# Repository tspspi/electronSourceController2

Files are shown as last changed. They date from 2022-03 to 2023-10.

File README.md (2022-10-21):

# Electron gun power supply and monitoring controller

_Note_: This project is designed for a particular experiment so it will not
be much of use for anyone who's not working on exactly that experiment.

This is firmware for a simple electron gun controller that is controlling

* Up to four FUG HCP 14-6500 high voltage power supplies (acceleration
  voltage, Wehnelt cylinder, focus voltage and a single deflection voltage
  power supply)
* The voltage and current measured by FUG HCP 14-6500 can also be used for
  general monitoring and beam loss measurement

## External communication ports

* UART0 provides main communication interface (and is also used by avrdude
  during flashing - there is an Arduino bootloader flashed on the board so
  flash method ```ẁiring``` can be used via USB

* Other UARTs may be used for RS485 or other components later on

## Pin assignment

| Pin | Assignment                          | Mode                      | ATEMGA2560 Port / Pin |
| --- | ----------------------------------- | ------------------------- | --------------------- |
| 22  | PSU1: Output enable                 | Digital out (optocoupled) | PA0                   |
| 23  | PSU1: Polarity set                  | Digital out (optocoupled) | PA1                   |
| 24  | PSU1: Current control mode          | Digital in                | PA2                   |
| 25  | PSU1: Voltage control mode          | Digital in                | PA3                   |
| 42  | PSU1: Voltage set                   | Analog out                | PL7                   |
| 43  | PSU1: Current limit set             | Analog out                | PL6                   |
| A0  | PSU1: Voltage sense                 | Analog in                 | PF0                   |
| A1  | PSU1: Current sense                 | Analog in                 | PF1                   |
| 26  | PSU2: Output enable                 | Digital out (optocoupled) | PA4                   |
| 27  | PSU2: Polarity set                  | Digital out (optocoupled) | PA5                   |
| 28  | PSU2: Current control mode          | Digital in                | PA6                   |
| 29  | PSU2: Voltage control mode          | Digital in                | PA7                   |
| 44  | PSU2: Voltage set                   | Analog out                | PL5                   |
| 45  | PSU2: Current limit set             | Analog out                | PL4                   |
| A2  | PSU2: Voltage sense                 | Analog in                 | PF2                   |
| A3  | PSU2: Current sense                 | Analog in                 | PF3                   |
| 30  | PSU3: Output enable                 | Digital out (optocoupled) | PC7                   |
| 31  | PSU3: Polarity set                  | Digital out (optocoupled) | PC6                   |
| 32  | PSU3: Current control mode          | Digital in                | PC5                   |
| 33  | PSU3: Voltage control mode          | Digital in                | PC4                   |
| 46  | PSU3: Voltage set                   | Analog out                | PL3                   |
| 47  | PSU3: Current limit set             | Analog out                | PL2                   |
| A4  | PSU3: Voltage sense                 | Analog in                 | PF4                   |
| A5  | PSU3: Current sense                 | Analog in                 | PF5                   |
| 34  | PSU4: Output enable                 | Digital out (optocoupled) | PC3                   |
| 35  | PSU4: Polarity set                  | Digital out (optocoupled) | PC2                   |
| 36  | PSU4: Current control mode          | Digital in                | PC1                   |
| 37  | PSU4: Voltage control mode          | Digital in                | PC0                   |
| 48  | PSU4: Voltage set                   | Analog out                | PL1                   |
| 49  | PSU4: Current limit set             | Analog out                | PL0                   |
| A6  | PSU4: Voltage sense                 | Analog in                 | PF6                   |
| A7  | PSU4: Current sense                 | Analog in                 | PF7                   |
| 38  | Filament power supply (230V side)   | Digital out               | PD7                   |
| A8  | Current sensor for filament         | Analog in                 | PK0                   |
| 50  | AD7705 MISO                         | Digital in                | PB3                   |
| 51  | AD7705 MOSI                         | Digital out               | PB2                   |
| 52  | AD7705 SCK                          | Digital out               | PB1                   |
| 53  | AD7705 CS                           | Digital out               | PB0                   |
|PWM10| AD7705 Reset                        | Digital out               | PB4                   |
|PWM11| AD7705 data ready                   | Digital in                | PB5                   |

## Protocol

In contrast to other implementations this board supports an ASCII based
communication protocol. For synchronization all messages start with a
fixed synchronization pattern consisting of three dollar signs. Each command
is terminated via a CR LF or only LF (CR is simply ignored by the serial
parser). Numbers are transmitted as ASCII decimal numbers.

| Command                                 | Sequence               | Response                                                                                                                     | Status                           |
| --------------------------------------- | ---------------------- | ---------------------------------------------------------------------------------------------------------------------------- | -------------------------------- |
| ID                                      | $$$ID<LF>              | Sends a simple ID response that identifies the firmware (ex. ```$$$electronctrl_20210707_001<LF>```)                         | working, tested                  |
| Filament on                             | $$$FILON<LF>           | Switches filament power supply on                                                                                            | working, tested                  |
| Filament off                            | $$$FILOFF<LF>          | Switches filament power supply off                                                                                           | working, tested                  |
| Estimate beam current                   | $$$BEAMA<LF>           | Calculates estimated beam current in 1/10 of microamperes                                                                    |                                  |
| Beam on                                 | $$$BEAMON<LF>          | Switches beam high voltage on (slowly, performing insulation test)                                                           | working, tested                  |
| Beam HV off                             | $$$BEAMHVOFF<LF>       | Switches beam high voltage off                                                                                               | working, tested                  |
| Get PSU current                         | $$$PSUGETA[n]<LF>      | Gets current for power supply 1,2,3,4                                                                                        | working, tested                  |
| Get PSU voltage                         | $$$PSUGETV[n]<LF>      | Gets voltage for power supply 1,2,3,4                                                                                        | working, tested                  |
| Get PSU modes                           | $$$PSUMODE<LF>         | Gets the mode for each PSU as a sequence of 4 ASCII chars (A or V for current or voltage controled mode, - for disabled)     | working, tested                  |
| Set PSU current limit                   | $$$PSUSETA[n][mmm]<LF> | Sets the power supply current limit for one of the 4 PSUs. The limit is supplied in 1/10 of an microampere                   | working, tested                  |
| Set PSU target voltage                  | $$$PSUSETV[n][mmm]<LF> | Sets the power supply voltage for one of the 4 PSUs. The voltage is set in V                                                 | working, tested                  |
| Set PSU polarity                        | $$$PSUPOL[n][p/n]<LF>  | Sets the polarity to be positive or negative                                                                                 | working, tested                  |
| Set PSU output enable                   | $$$PSUON[n]<LF>        | Enabled the output of the given PSU                                                                                          | working, tested                  |
| Set PSU output disable                  | $$$PSUOFF[n]<LF>       | Disabled the output of the given PSU                                                                                         | working, tested                  |
| Disable all voltages (PSU and filament) | $$$OFF<LF>             | Disabled all voltages including the filament supply                                                                          | working, tested                  |
| Get filament voltage                    | $$$FILV<LF>            | Measures filament voltage (if supported)                                                                                     |                                  |
| Get filament current                    | $$$FILA<LF>            | Measures filament current (if supported)                                                                                     |                                  |
| Set filament current                    | $$$SETFILA[n]<LF>      | Sets filament current via current controller board                                                                           |                                  |
| Perform HV insulation test              | $$$INSUL<LF>           | Performs insulation test. Reports voltages while testing.                                                                    | working, tested                  |
| Perform cathode bakeout                 | $$$FILBAKE<LF>         | Performs a baking sequence on filament to remove any residue of trapped gas on the surface                                   |                                  |
| Perform software reset                  | $$$RESET<LF>           | Performs a software reset on the control system (reinitializes everything, no power cycle)                                   |                                  |

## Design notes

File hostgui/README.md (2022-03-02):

# Custom electron gun slow control Python communication library and GUI utlity

__Work in progress__

## Communication library

The communication library from ```eguncom.py``` implements most of the
communication protocol with the electron beam slow-control system.

### ```class ElectronGunControl```

The ```ElectronGunControl``` class implements asynchronous and synchronous
communication with the serially / USB attached control system. The port file
is passed to the constructor

```
ctrl = ElectronGunNotConnected(portFile = '/dev/...')
```

When no port file is passed it defaults to ```/dev/ttyU0```.

The exposed public methods are:

| Method                            | Description                                                                                                        | Synchronous      | Asynchronous callback                                |
| --------------------------------- | ------------------------------------------------------------------------------------------------------------------ | ---------------- | ---------------------------------------------------- |
| id()                              | Queries the current version                                                                                        | with sync = True | cbIdentify(controller, versionDate, versionRevision) |
| getPSUVoltage(channel)            | Queries the current voltage on the given channel                                                                   | with sync = True | cbVoltage(controller, channel, voltageVolts)         |
| getPSUCurrent(channel)            | Queries the current current on the given channel                                                                   | with sync = True | cbCurrent(controller, channel, currentMicroamps)     |
| getPSUModes()                     | Checks if PSUs are off, in voltage limited or current limited mode                                                 | with sync = True | cbPSUMode(controller, states)                        |
| getFilamentCurrent()              | Queries the filament current                                                                                       | with sync = True | cbFilamentCurrent(controller, current)               |
| off()                             | Disabled all high voltage and filament currents                                                                    |                  |                                                      |
| setPSUPolarity(channel, polarity) | Sets polarity to POLARITY_POS or POLARITY_NEG                                                                      |                  |                                                      |
| setPSUEnable(channel)             | Enables the given PSU channel                                                                                      |                  |                                                      |
| setPSUDisable(channel)            | Disables the given PSU channel                                                                                     |                  |                                                      |
| setPSUVoltage(channel, voltage)   | Sets the given channel to the given voltage                                                                        |                  |                                                      |
| setFilamentCurrent(currentMa)     | Sets the filament current or target current to the specified milliamps                                             |                  |                                                      |
| setFilamentOn()                   | Enabled the filament supply                                                                                        |                  |                                                      |
| setFilamentOff()                  | Disabled the filament supply                                                                                       |                  |                                                      |
| runInsulationTest()               | Runs an insulation test with low current limits                                                                    | with sync = True | cbInsulation(isOk, listOfShorts)                     |
| beamOn()                          | Runs the slow beam on sequence (slowly heating filament to previously set setFilamentCurrent, ramping up voltages) | with sync = True | cbBeamon()                                           |

### Usage example

#### Synchronous sample (USB / serial)

Example to perform a __synchronous__:

* Insulation check
* Startup for 100 mA beam current
* Looping through focus voltages
* Shutting down

```
with ElectronGunControl() as ctrl:
    # Currently a hack to wait for the control system to reset when using the
    # primary port

    time.sleep(5)

    # We want to see the voltages reported by the system so we
    # define a lambda that just prints the voltages while ramping up
    # during insulation test and beam on sequence

    ctrl.cbVoltage = lambda c,chan,v : print("Voltage for channel {} is {} V".format(chan, v))

    # Query it's identity
    ret = ctrl.id(sync = True)
    print("ID call returned {}".format(ret))

    # Run insulation test
    print("Running insulation test")
    ret = ctrl.runInsulationTest(sync = True)
    print("Insulation test returned: {}".format(ret))

    # Run beam on sequence ...
    ret = ctrl.beamOn(sync = True)
    print("Beam on successfully returned: {}".format(ret))

    print("Sweeping focus voltage")
    for focusVoltage in range(1750,1950):
        print("New focus voltage {}".format(focusVoltage))
        ctrl.setPSUVoltage(3, focusVoltage)
        time.sleep(1)

    ctrl.off()
    print("Off, done ...")
```

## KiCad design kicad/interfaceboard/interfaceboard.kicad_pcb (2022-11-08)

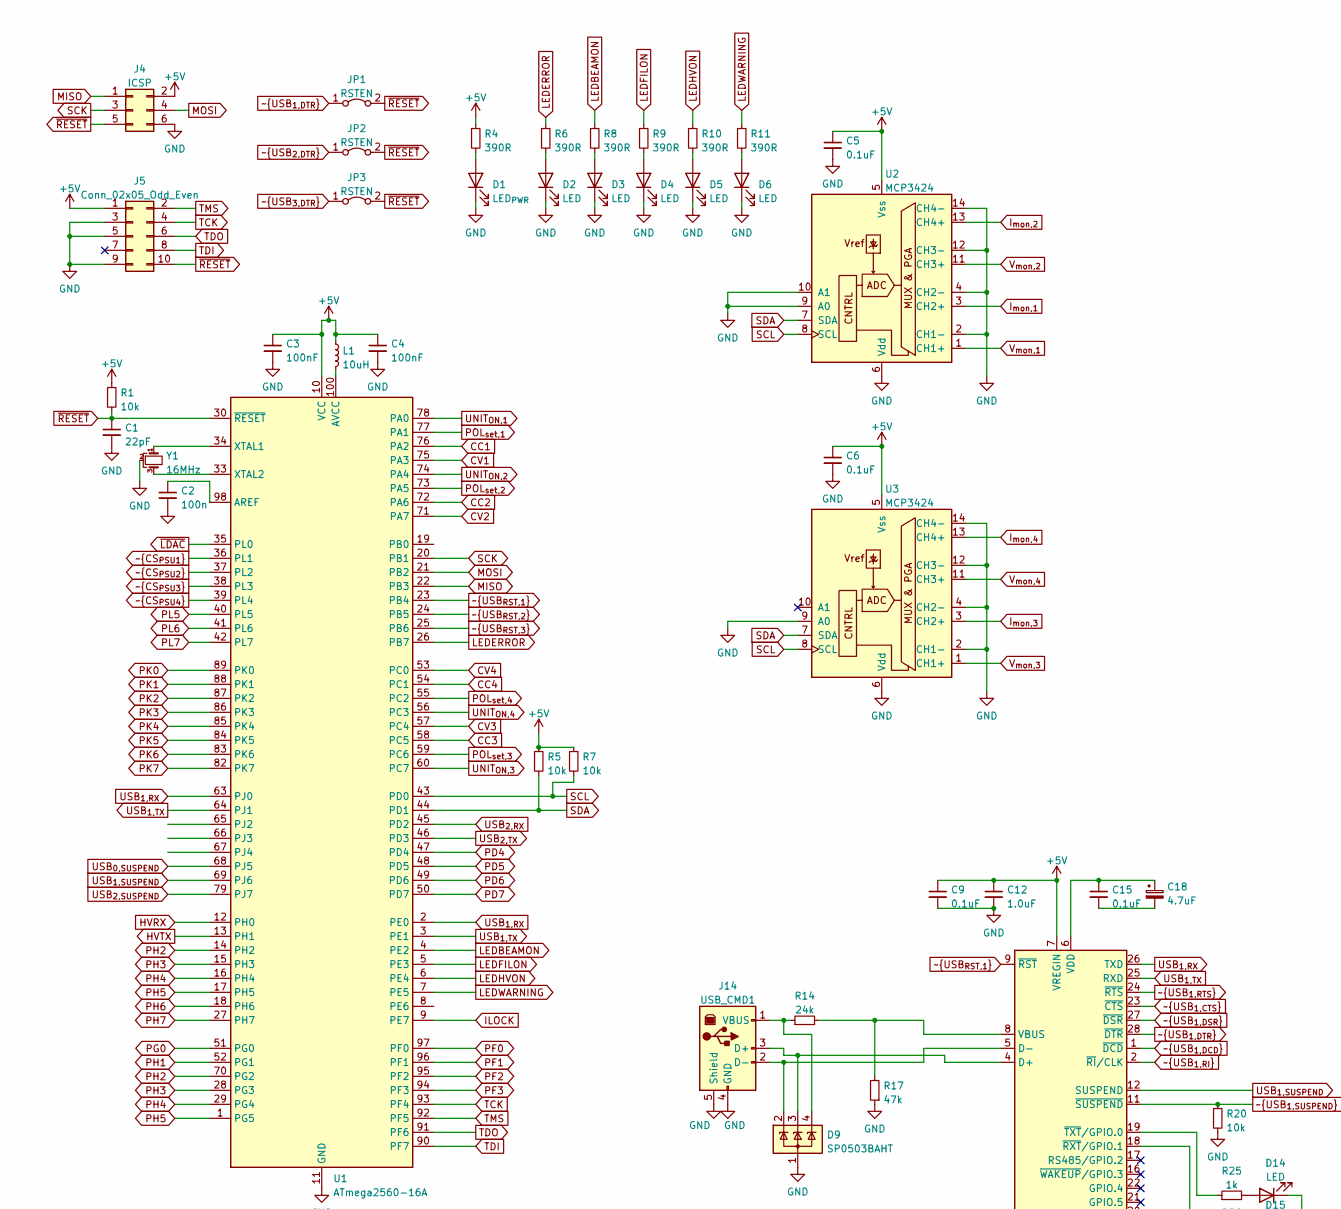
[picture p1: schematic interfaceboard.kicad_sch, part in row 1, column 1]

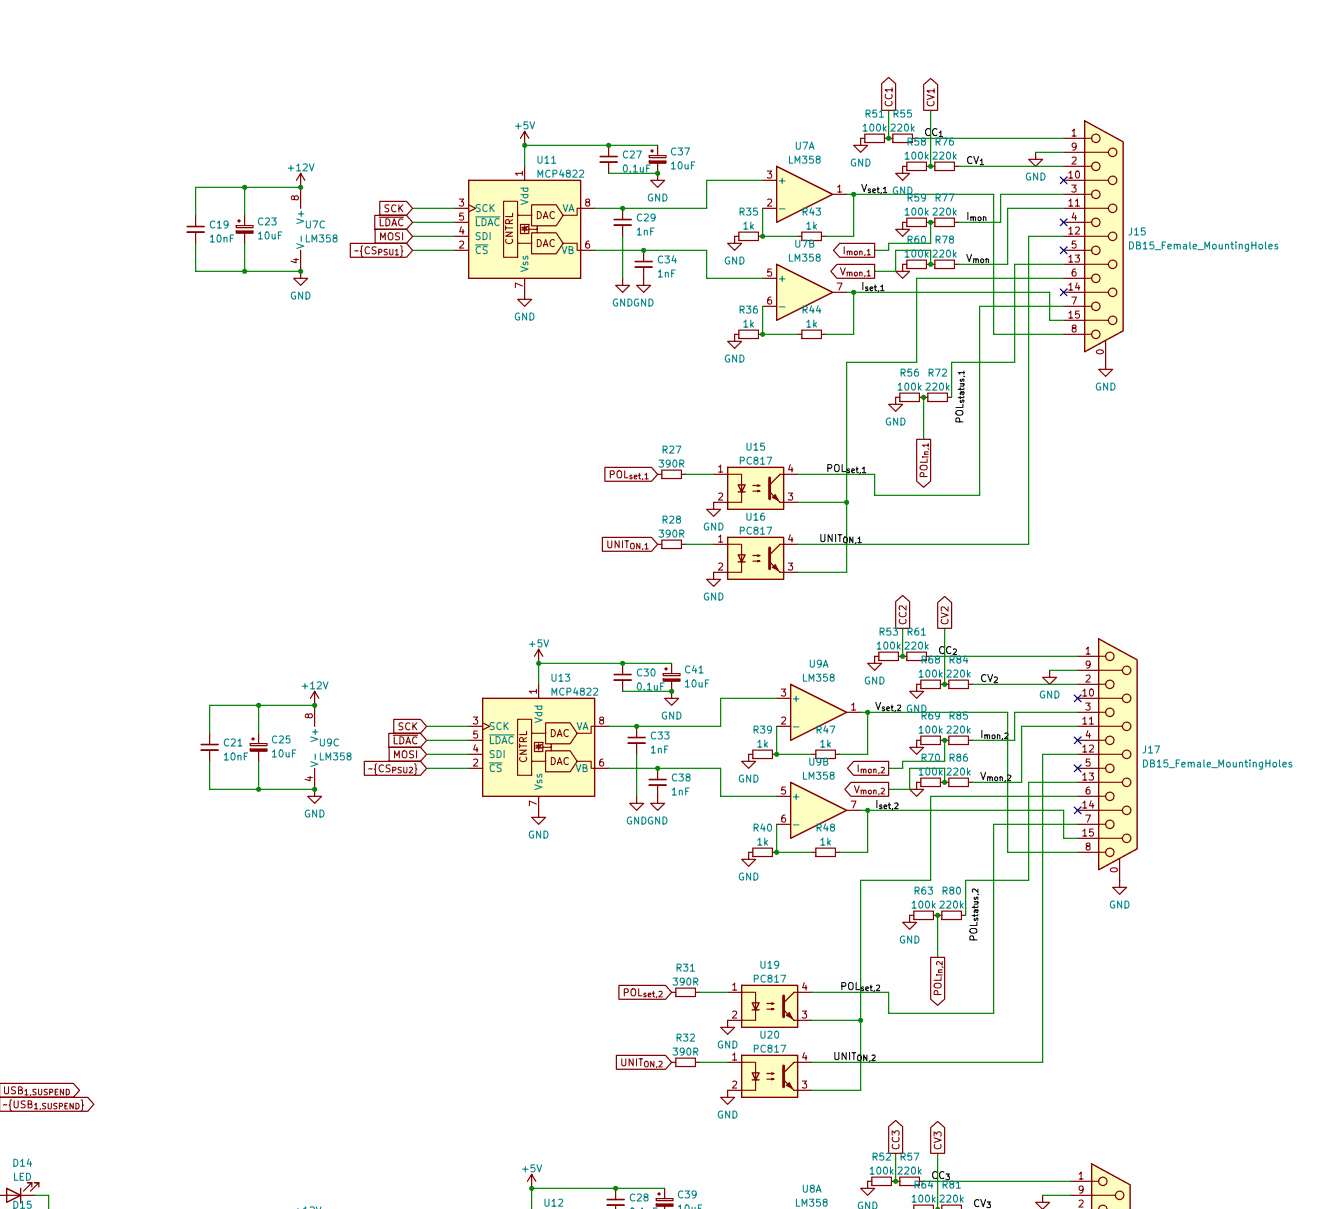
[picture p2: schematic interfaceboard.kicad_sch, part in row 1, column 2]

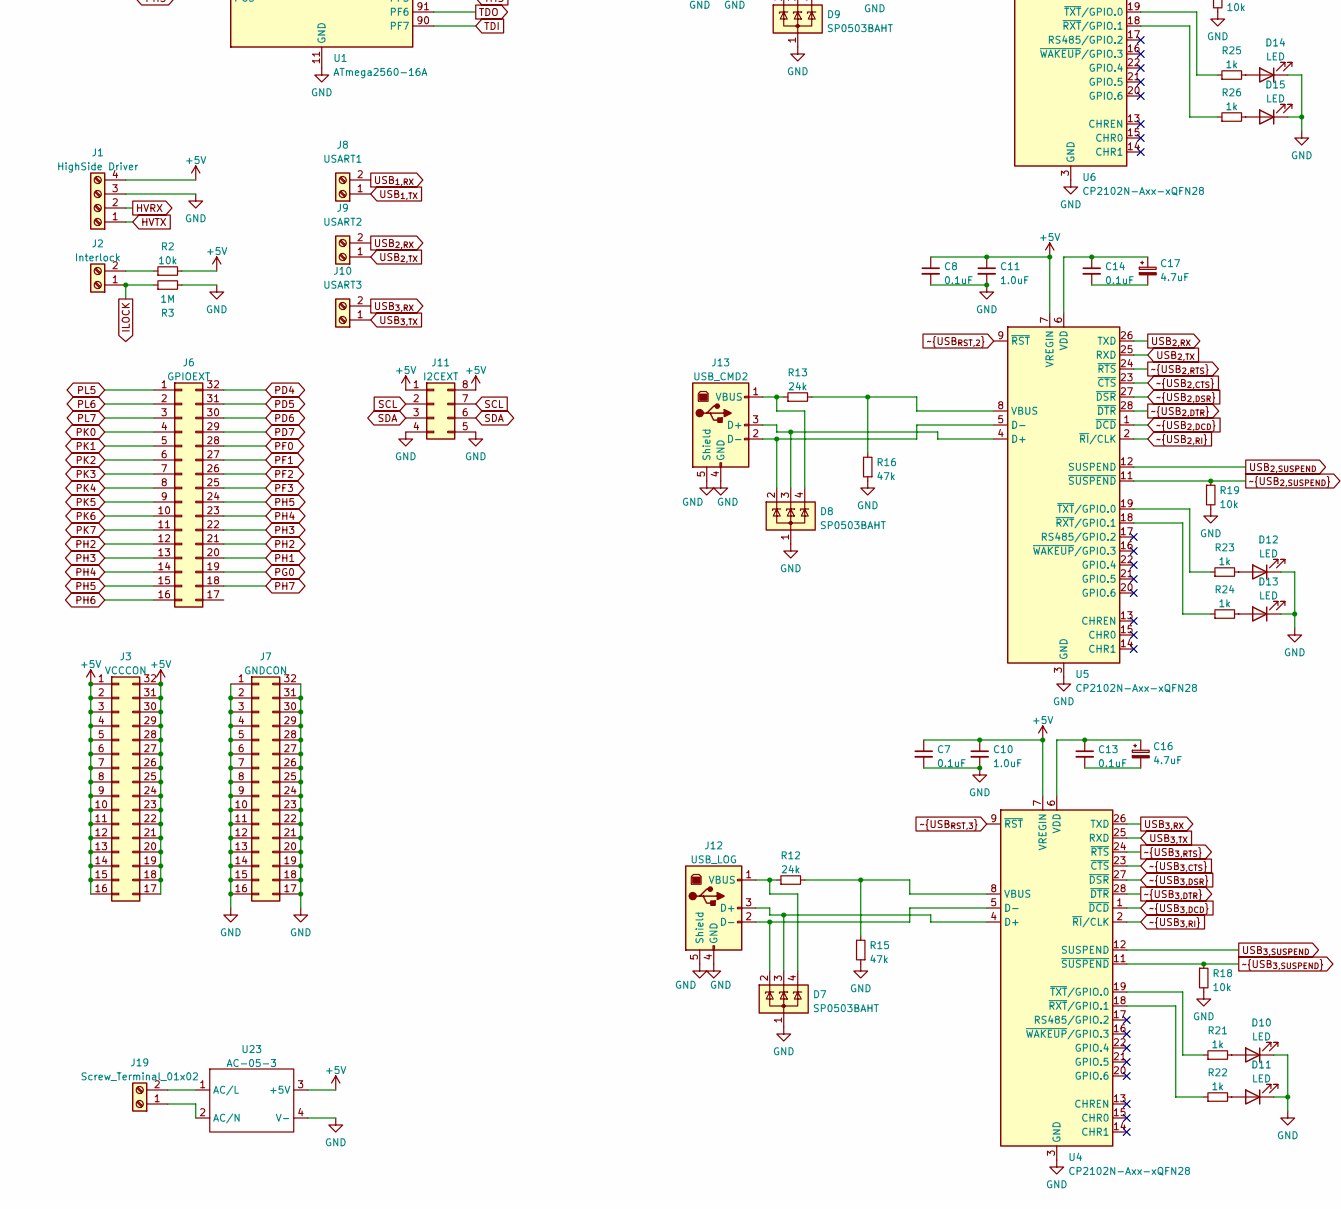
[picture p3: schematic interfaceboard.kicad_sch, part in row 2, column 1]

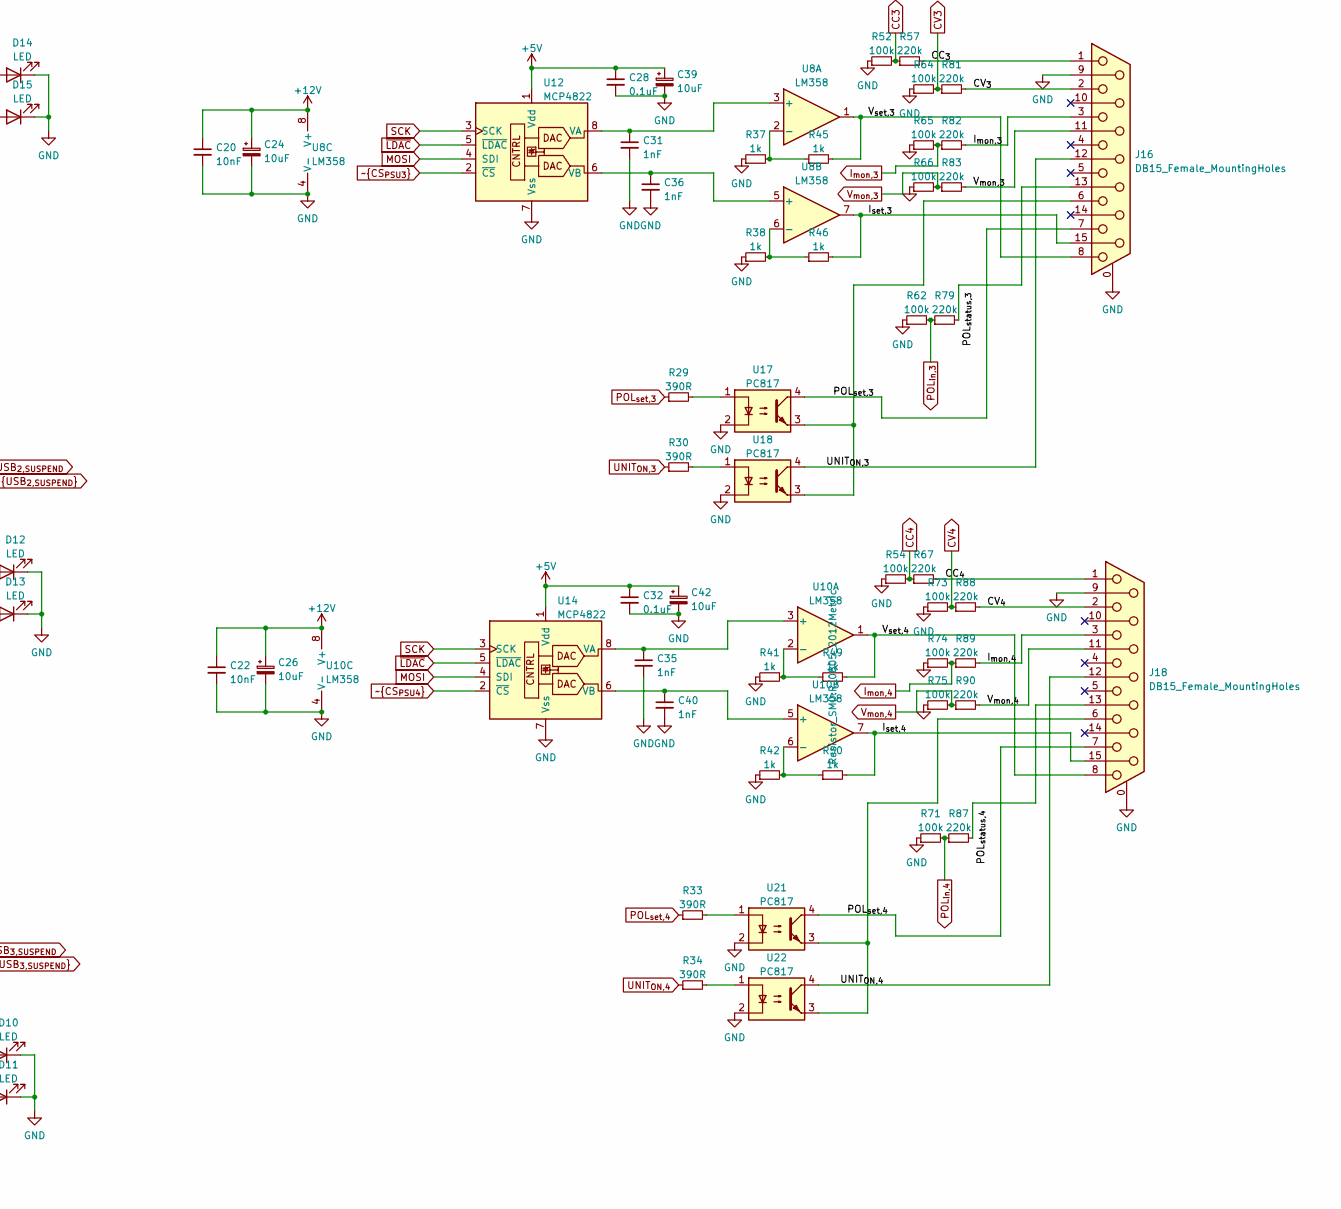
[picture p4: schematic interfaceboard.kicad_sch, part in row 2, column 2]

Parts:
C1: 22pF; C_0805_2012Metric
C2: 100n; C_0805_2012Metric
C3, C4: 100nF; C_0805_2012Metric
C5, C6, C7, C8, C9, C13, C14, C15, C27, C28, C30, C32: 0.1uF; C_0805_2012Metric
C10, C11, C12: 1.0uF; C_0805_2012Metric
C16, C17, C18: 4.7uF; C_0805_2012Metric
C19, C20, C21, C22: 10nF; C_0805_2012Metric
C23, C24, C25, C26, C37, C39, C41, C42: 10uF; C_0805_2012Metric
C29, C31, C33, C34, C35, C36, C38, C40: 1nF; C_0805_2012Metric
D1: LED_{PWR}; LED_D3.0mm
D2, D3, D4, D5, D6, D10, D11, D12, D13, D14, D15: LED; LED_D3.0mm
D7, D8, D9: SP0503BAHT; SOT-143
J1: HighSide Driver; PinHeader_1x04_P2.54mm_Vertical
J2: Interlock; PinHeader_1x02_P2.54mm_Vertical
J3: VCCCON; PinHeader_2x16_P2.54mm_Vertical
J4: ICSP; PinSocket_2x03_P2.54mm_Vertical
J5: Conn_02x05_Odd_Even; PinSocket_2x05_P2.54mm_Vertical
J6: GPIOEXT; PinHeader_2x16_P2.54mm_Vertical
J7: GNDCON; PinHeader_2x16_P2.54mm_Vertical
J8: USART1; PinHeader_1x02_P2.54mm_Vertical
J9: USART2; PinHeader_1x02_P2.54mm_Vertical
J10: USART3; PinHeader_1x02_P2.54mm_Vertical
J11: I2CEXT; PinHeader_2x04_P2.54mm_Vertical
J12: USB_LOG; USB_B_Lumberg_2411_02_Horizontal; FarnellNo 3490505 (2401 06)
J13: USB_CMD2; USB_B_Lumberg_2411_02_Horizontal
J14: USB_CMD1; USB_B_Lumberg_2411_02_Horizontal
J15: DB15_Female_MountingHoles; DSUB-15_Female_Horizontal_P2.77x2.84mm_EdgePinOffset9.90mm_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; FarnellNo 3817870
J16, J17, J18: DB15_Female_MountingHoles; DSUB-15_Female_Horizontal_P2.77x2.84mm_EdgePinOffset9.90mm_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
J19: Screw_Terminal_01x02; PinHeader_1x02_P2.54mm_Vertical
JP1, JP2, JP3: RSTEN; PinSocket_1x02_P2.54mm_Vertical
L1: 10uH; L_1206_3216Metric
R1, R2, R5, R7, R18, R19, R20: 10k; R_0805_2012Metric
R3: 1M; R_0805_2012Metric
R4, R6, R8, R9, R10, R11, R27, R28, R29, R30, R31, R32, R33, R34: 390R; R_0805_2012Metric
R12, R13, R14: 24k; R_0805_2012Metric
R15, R16, R17: 47k; R_0805_2012Metric
R21, R22, R23, R24, R25, R26, R35, R36, R37, R38, R39, R40, R41, R42, R43, R44, R45, R46, R47, R48, R49, R50: 1k; R_0805_2012Metric
R51, R52, R53, R54, R56, R58, R59, R60, R62, R63, R64, R65, R66, R68, R69, R70, R71, R73, R74, R75: 100k; R_0805_2012Metric
R55, R57, R61, R67, R72, R76, R77, R78, R79, R80, R81, R82, R83, R84, R85, R86, R87, R88, R89, R90: 220k; R_0805_2012Metric
U1: ATmega2560-16A; TQFP-100_14x14mm_P0.5mm
U2, U3: MCP3424; SOIC-14_3.9x8.7mm_P1.27mm
U4, U5, U6: CP2102N-Axx-xQFN28; QFN-28-1EP_5x5mm_P0.5mm_EP3.35x3.35mm
U7, U8, U9, U10: LM358; DIP-8_W7.62mm
U11, U12, U13, U14: MCP4822; DIP-8_W7.62mm
U15, U16, U17, U18, U19, U20, U21, U22: PC817; DIP-4_W7.62mm
U23: AC-05-3
Y1: 16MHz; PinSocket_1x03_P2.54mm_Vertical

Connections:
+5V: C3.1, C4.1, C5.1, C6.1, C7.1, C8.1, C9.1, C10.1, C11.1, C12.1, C27.1, C28.1, C30.1, C32.1, C37.1, C39.1, C41.1, C42.1, J1.4, J3.1, J3.2, J3.3, J3.4, J3.5, J3.6, J3.7, J3.8, J3.9, J3.10, J3.11, J3.12, J3.13, J3.14, J3.15, J3.16, J3.17, J3.18, J3.19, J3.20, J3.21, J3.22, J3.23, J3.24, J3.25, J3.26, J3.27, J3.28, J3.29, J3.30, J3.31, J3.32, J4.2, J5.1, J11.1, J11.8, L1.1, R1.1, R2.2, R4.1, R5.1, R7.1, U1.10 (VCC), U1.31 (VCC), U1.61 (VCC), U1.80 (VCC), U2.5 (Vss), U3.5 (Vss), U4.7 (VREGIN), U5.7 (VREGIN), U6.7 (VREGIN), U11.1 (Vdd), U12.1 (Vdd), U13.1 (Vdd), U14.1 (Vdd), U23.3 (+5V)
+12V: C19.1, C20.1, C21.1, C22.1, C23.1, C24.1, C25.1, C26.1, U7.8 (V+), U8.8 (V+), U9.8 (V+), U10.8 (V+)
/CC_{1}: J15.1, R55.2
/CC_{2}: J17.1, R61.2
/CC_{3}: J16.1, R57.2
/CC_{4}: J18.1, R67.2
/CV_{1}: J15.2, R76.2
/CV_{2}: J17.2, R84.2
/CV_{3}: J16.2, R81.2
/CV_{4}: J18.2, R88.2
/I_{mon}: J15.3, R77.2
/I_{set,1}: J15.15, R44.2, U7.7
/I_{set,2}: J17.15, R48.2, U9.7
/I_{set,3}: J16.15, R46.2, U8.7
/I_{set,4}: J18.15, R50.2, U10.7
/V_{mon}: J15.11 (P111), R78.2
/V_{set,1}: J15.8, R43.2, U7.1
/V_{set,2}: J17.8, R47.2, U9.1
/V_{set,3}: J16.8, R45.2, U8.1
/V_{set,4}: J18.8, R49.2, U10.1
CC1: R51.2, R55.1, U1.76 (PA2)
CC2: R53.2, R61.1, U1.72 (PA6)
CC3: R52.2, R57.1, U1.58 (PC5)
CC4: R54.2, R67.1, U1.54 (PC1)
CV1: R58.2, R76.1, U1.75 (PA3)
CV2: R68.2, R84.1, U1.71 (PA7)
CV3: R64.2, R81.1, U1.57 (PC4)
CV4: R73.2, R88.1, U1.53 (PC0)
GND: C1.2, C2.2, C3.2, C4.2, C5.2, C6.2, C7.2, C8.2, C9.2, C10.2, C11.2, C12.2, C19.2, C20.2, C21.2, C22.2, C23.2, C24.2, C25.2, C26.2, C27.2, C28.2, C29.2, C30.2, C31.2, C32.2, C33.2, C34.2, C35.2, C36.2, C37.2, C38.2, C39.2, C40.2, C41.2, C42.2, D1.1 (K), D2.1 (K), D3.1 (K), D4.1 (K), D5.1 (K), D6.1 (K), D7.1 (A), D8.1 (A), D9.1 (A), D10.1 (K), D11.1 (K), D12.1 (K), D13.1 (K), D14.1 (K), D15.1 (K), J1.3, J4.6, J5.3, J5.5, J5.9, J7.1, J7.2, J7.3, J7.4, J7.5, J7.6, J7.7, J7.8, J7.9, J7.10, J7.11, J7.12, J7.13, J7.14, J7.15, J7.16, J7.17, J7.18, J7.19, J7.20, J7.21, J7.22, J7.23, J7.24, J7.25, J7.26, J7.27, J7.28, J7.29, J7.30, J7.31, J7.32, J11.4, J11.5, J12.4 (GND), J12.5 (Shield), J13.4 (GND), J13.5 (Shield), J14.4 (GND), J14.5 (Shield), J15.0 (PAD), J15.9, J16.0 (PAD), J16.9, J17.0 (PAD), J17.9, J18.0 (PAD), J18.9, R3.2, R15.1, R16.1, R17.1, R18.2, R19.2, R20.2, R35.1, R36.1, R37.1, R38.1, R39.1, R40.1, R41.1, R42.1, R51.1, R52.1, R53.1, R54.1, R56.1, R58.1, R59.1, R60.1, R62.1, R63.1, R64.1, R65.1, R66.1, R68.1, R69.1, R70.1, R71.1, R73.1, R74.1, R75.1, U1.11 (GND), U1.32 (GND), U1.62 (GND), U1.81 (GND), U1.99 (GND), U2.2 (CH1-), U2.4 (CH2-), U2.6 (Vdd), U2.9 (A0), U2.10 (A1), U2.12 (CH3-), U2.14 (CH4-), U3.2 (CH1-), U3.4 (CH2-), U3.6 (Vdd), U3.9 (A0), U3.12 (CH3-), U3.14 (CH4-), U4.3 (GND), U4.29 (GND), U5.3 (GND), U5.29 (GND), U6.3 (GND), U6.29 (GND), U7.4 (V-), U8.4 (V-), U9.4 (V-), U10.4 (V-), U11.7 (Vss), U12.7 (Vss), U13.7 (Vss), U14.7 (Vss), U15.2, U16.2, U17.2, U18.2, U19.2, U20.2, U21.2, U22.2, U23.4 (V-), Y1.2
HVRX: J1.2, U1.12 (PH0)
HVTX: J1.1, U1.13 (PH1)
ILOCK: J2.1, R3.1, U1.9 (PE7)
I_{mon,1}: R59.2, R77.1, U2.3 (CH2+)
I_{mon,2}: J17.3, R69.2, R85.1, R85.2, U2.13 (CH4+)
I_{mon,3}: J16.3, R65.2, R82.1, R82.2, U3.3 (CH2+)
I_{mon,4}: J18.3, R74.2, R89.1, R89.2, U3.13 (CH4+)
LEDBEAMON: R8.1, U1.4 (PE2)
LEDERROR: R6.1, U1.26 (PB7)
LEDFILON: R9.1, U1.5 (PE3)
LEDHVON: R10.1, U1.6 (PE4)
LEDWARNING: R11.1, U1.7 (PE5)
MISO: J4.1, U1.22 (PB3)
MOSI: J4.4, U1.21 (PB2), U11.4 (SDI), U12.4 (SDI), U13.4 (SDI), U14.4 (SDI)
unnamed: C2.1, U1.98 (AREF)
unnamed: C13.1, C16.1, U4.6 (VDD)
unnamed: C13.2, C16.2
unnamed: C14.1, C17.1, U5.6 (VDD)
unnamed: C14.2, C17.2
unnamed: C15.1, C18.1, U6.6 (VDD)
unnamed: C15.2, C18.2
unnamed: C29.1, U7.3 (+), U11.8 (VA)
unnamed: C31.1, U8.3 (+), U12.8 (VA)
unnamed: C33.1, U9.3 (+), U13.8 (VA)
unnamed: C34.1, U7.5 (+), U11.6 (VB)
unnamed: C35.1, U10.3 (+), U14.8 (VA)
unnamed: C36.1, U8.5 (+), U12.6 (VB)
unnamed: C38.1, U9.5 (+), U13.6 (VB)
unnamed: C40.1, U10.5 (+), U14.6 (VB)
unnamed: D1.2 (A), R4.2
unnamed: D2.2 (A), R6.2
unnamed: D3.2 (A), R8.2
unnamed: D4.2 (A), R9.2
unnamed: D5.2 (A), R10.2
unnamed: D6.2 (A), R11.2
unnamed: D7.2 (K), J12.2 (D-), U4.5 (D-)
unnamed: D7.3 (K), J12.3 (D+), U4.4 (D+)
unnamed: D7.4 (K), J12.1 (VBUS), R12.1
unnamed: D8.2 (K), J13.2 (D-), U5.5 (D-)
unnamed: D8.3 (K), J13.3 (D+), U5.4 (D+)
unnamed: D8.4 (K), J13.1 (VBUS), R13.1
unnamed: D9.2 (K), J14.2 (D-), U6.5 (D-)
unnamed: D9.3 (K), J14.3 (D+), U6.4 (D+)
unnamed: D9.4 (K), J14.1 (VBUS), R14.1
unnamed: D10.2 (A), R21.2
unnamed: D11.2 (A), R22.2
unnamed: D12.2 (A), R23.2
unnamed: D13.2 (A), R24.2
unnamed: D14.2 (A), R25.2
unnamed: D15.2 (A), R26.2
unnamed: J2.2, R2.1
unnamed: J15.6, U15.3, U16.3
unnamed: J15.13, R72.2
unnamed: J16.6, U17.3, U18.3
unnamed: J16.13, R79.2
unnamed: J17.6, U19.3, U20.3
unnamed: J17.13, R80.2
unnamed: J18.6, U21.3, U22.3
unnamed: J18.13, R87.2
unnamed: J19.1, U23.2 (AC/N)
unnamed: J19.2, U23.1 (AC/L)
unnamed: L1.2, U1.100 (AVCC)
unnamed: R12.2, R15.2, U4.8 (VBUS)
unnamed: R13.2, R16.2, U5.8 (VBUS)
unnamed: R14.2, R17.2, U6.8 (VBUS)
unnamed: R21.1, U4.19 (~TXT/GPIO.0)
unnamed: R22.1, U4.18 (~RXT/GPIO.1)
unnamed: R23.1, U5.19 (~TXT/GPIO.0)
unnamed: R24.1, U5.18 (~RXT/GPIO.1)
unnamed: R25.1, U6.19 (~TXT/GPIO.0)
unnamed: R26.1, U6.18 (~RXT/GPIO.1)
unnamed: R27.2, U15.1
unnamed: R28.2, U16.1
unnamed: R29.2, U17.1
unnamed: R30.2, U18.1
unnamed: R31.2, U19.1
unnamed: R32.2, U20.1
unnamed: R33.2, U21.1
unnamed: R34.2, U22.1
unnamed: R35.2, R43.1, U7.2 (-)
unnamed: R36.2, R44.1, U7.6 (-)
unnamed: R37.2, R45.1, U8.2 (-)
unnamed: R38.2, R46.1, U8.6 (-)
unnamed: R39.2, R47.1, U9.2 (-)
unnamed: R40.2, R48.1, U9.6 (-)
unnamed: R41.2, R49.1, U10.2 (-)
unnamed: R42.2, R50.1, U10.6 (-)
unnamed: U1.33 (XTAL2), Y1.3
unnamed: U1.34 (XTAL1), Y1.1
PD4: J6.32, U1.47 (PD4)
PD5: J6.31, U1.48 (PD5)
PD6: J6.30, U1.49 (PD6)
PD7: J6.29, U1.50 (PD7)
PF0: J6.28, U1.97 (PF0)
PF1: J6.27, U1.96 (PF1)
PF2: J6.26, U1.95 (PF2)
PF3: J6.25, U1.94 (PF3)
PG0: J6.19, U1.51 (PG0)
PH1: J6.20, U1.52 (PG1)
PH2: J6.12, J6.21, U1.14 (PH2), U1.70 (PG2)
PH3: J6.13, J6.22, U1.15 (PH3), U1.28 (PG3)
PH4: J6.14, J6.23, U1.16 (PH4), U1.29 (PG4)
PH5: J6.15, J6.24, U1.1 (PG5), U1.17 (PH5)
PH6: J6.16, U1.18 (PH6)
PH7: J6.18, U1.27 (PH7)
PK0: J6.4, U1.89 (PK0)
PK1: J6.5, U1.88 (PK1)
PK2: J6.6, U1.87 (PK2)
PK3: J6.7, U1.86 (PK3)
PK4: J6.8, U1.85 (PK4)
PK5: J6.9, U1.84 (PK5)
PK6: J6.10, U1.83 (PK6)
PK7: J6.11, U1.82 (PK7)
PL5: J6.1, U1.40 (PL5)
PL6: J6.2, U1.41 (PL6)
PL7: J6.3, U1.42 (PL7)
POL_{in,1}: R56.2, R72.1
POL_{in,2}: R63.2, R80.1
POL_{in,3}: R62.2, R79.1
POL_{in,4}: R71.2, R87.1
POL_{set,1}: J15.7, R27.1, U1.77 (PA1), U15.4
POL_{set,2}: J17.7, R31.1, U1.73 (PA5), U19.4
POL_{set,3}: J16.7, R29.1, U1.59 (PC6), U17.4
POL_{set,4}: J18.7, R33.1, U1.55 (PC2), U21.4
SCK: J4.3, U1.20 (PB1), U11.3 (SCK), U12.3 (SCK), U13.3 (SCK), U14.3 (SCK)
SCL: J11.2, J11.7, R7.2, U1.43 (PD0), U2.8 (SCL), U3.8 (SCL)
SDA: J11.3, J11.6, R5.2, U1.44 (PD1), U2.7 (SDA), U3.7 (SDA)
TCK: J5.4, U1.93 (PF4)
TDI: J5.8, U1.90 (PF7)
TDO: J5.6, U1.91 (PF6)
TMS: J5.2, U1.92 (PF5)
UNIT_{ON,1}: J15.12, R28.1, U1.78 (PA0), U16.4
UNIT_{ON,2}: J17.12, R32.1, U1.74 (PA4), U20.4
UNIT_{ON,3}: J16.12, R30.1, U1.60 (PC7), U18.4
UNIT_{ON,4}: J18.12, R34.1, U1.56 (PC3), U22.4
USB_{0,SUSPEND}: U1.68 (PJ5)
USB_{1,RX}: J8.2, U1.2 (PE0), U1.63 (PJ0), U6.26 (TXD)
USB_{1,SUSPEND}: U1.69 (PJ6), U6.12 (SUSPEND)
USB_{1,TX}: J8.1, U1.3 (PE1), U1.64 (PJ1), U6.25 (RXD)
USB_{2,RX}: J9.2, U1.45 (PD2), U5.26 (TXD)
USB_{2,SUSPEND}: U1.79 (PJ7), U5.12 (SUSPEND)
USB_{2,TX}: J9.1, U1.46 (PD3), U5.25 (RXD)
USB_{3,RX}: J10.2, U4.26 (TXD)
USB_{3,SUSPEND}: U4.12 (SUSPEND)
USB_{3,TX}: J10.1, U4.25 (RXD)
V_{mon,1}: R60.2, R78.1, U2.1 (CH1+)
V_{mon,2}: J17.11 (P111), R70.2, R86.1, R86.2, U2.11 (CH3+)
V_{mon,3}: J16.11 (P111), R66.2, R83.1, R83.2, U3.1 (CH1+)
V_{mon,4}: J18.11 (P111), R75.2, R90.1, R90.2, U3.11 (CH3+)
~CS_{PSU1}: U1.36 (PL1), U11.2 (~CS)
~CS_{PSU2}: U1.37 (PL2), U13.2 (~CS)
~CS_{PSU3}: U1.38 (PL3), U12.2 (~CS)
~CS_{PSU4}: U1.39 (PL4), U14.2 (~CS)
~LDAC: U1.35 (PL0), U11.5 (~LDAC), U12.5 (~LDAC), U13.5 (~LDAC), U14.5 (~LDAC)
~RESET: C1.1, J4.5, J5.10, JP1.2 (B), JP2.2 (B), JP3.2 (B), R1.2, U1.30 (~RESET)
~USB_{1,CTS}: U6.23 (~CTS)
~USB_{1,DCD}: U6.1 (~DCD)
~USB_{1,DSR}: U6.27 (~DSR)
~USB_{1,DTR}: JP1.1 (A), U6.28 (~DTR)
~USB_{1,RI}: U6.2 (~RI/CLK)
~USB_{1,RTS}: U6.24 (~RTS)
~USB_{1,SUSPEND}: R20.1, U6.11 (~SUSPEND)
~USB_{2,CTS}: U5.23 (~CTS)
~USB_{2,DCD}: U5.1 (~DCD)
~USB_{2,DSR}: U5.27 (~DSR)
~USB_{2,DTR}: JP2.1 (A), U5.28 (~DTR)
~USB_{2,RI}: U5.2 (~RI/CLK)
~USB_{2,RTS}: U5.24 (~RTS)
~USB_{2,SUSPEND}: R19.1, U5.11 (~SUSPEND)
~USB_{3,CTS}: U4.23 (~CTS)
~USB_{3,DCD}: U4.1 (~DCD)
~USB_{3,DSR}: U4.27 (~DSR)
~USB_{3,DTR}: JP3.1 (A), U4.28 (~DTR)
~USB_{3,RI}: U4.2 (~RI/CLK)
~USB_{3,RTS}: U4.24 (~RTS)
~USB_{3,SUSPEND}: R18.1, U4.11 (~SUSPEND)
~USB_{RST,1}: U1.23 (PB4), U6.9 (~RST)
~USB_{RST,2}: U1.24 (PB5), U5.9 (~RST)
~USB_{RST,3}: U1.25 (PB6), U4.9 (~RST)

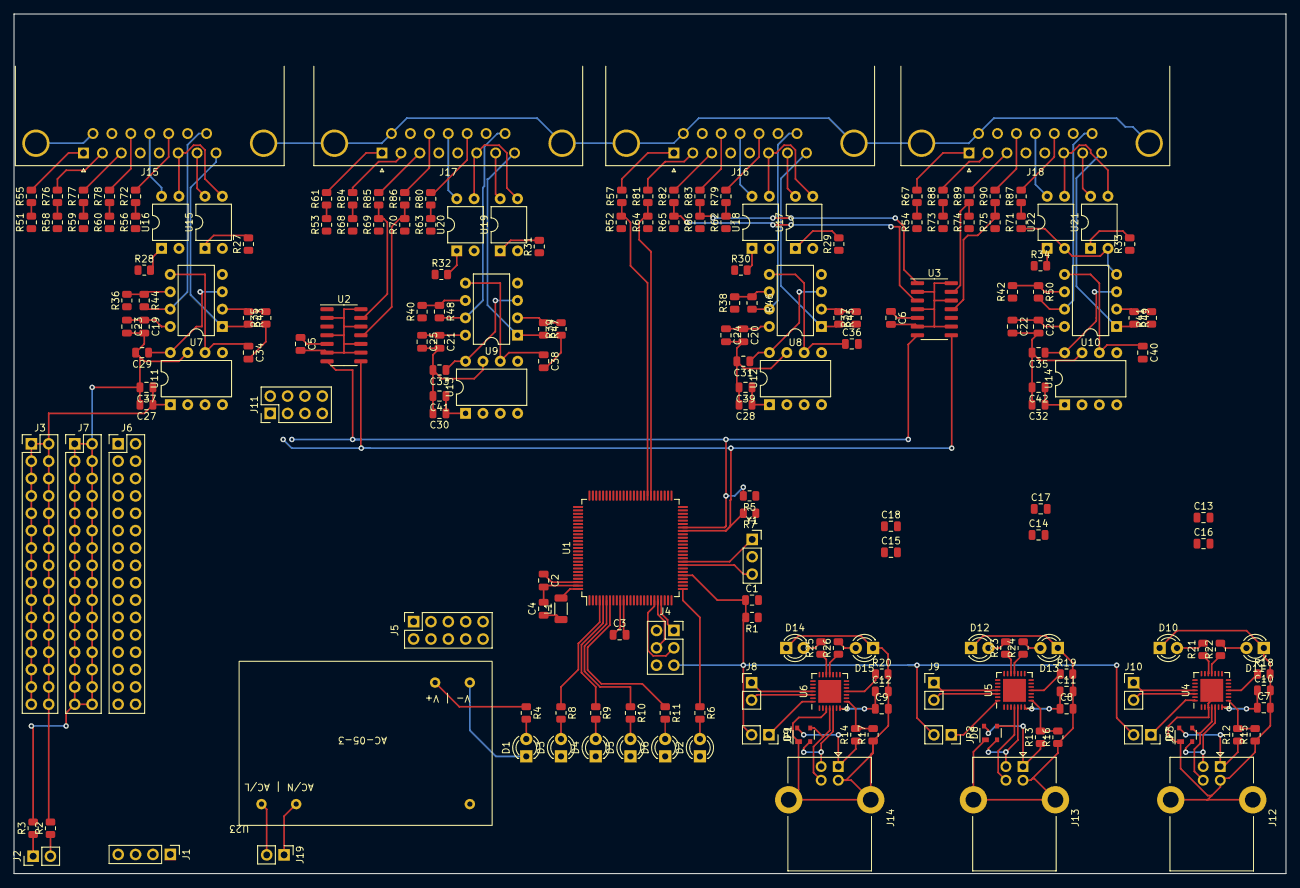
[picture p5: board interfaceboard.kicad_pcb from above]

Board: 2 copper layers, 186.1 x 125.7 mm, 194 parts (0 on the bottom side), 191 nets.

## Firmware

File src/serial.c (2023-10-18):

#include <avr/io.h>
#include <avr/interrupt.h>
#include <math.h>
#include <util/twi.h>
#include <stdint.h>
#include <string.h>

#include "./serial.h"
#include "./controller.h"
#include "./sysclock.h"
#include "./adc.h"
#include "./psu.h"
#include "./pwmout.h"
#include "./cfgeeprom.h"

static void adcCalibrateHVPS_Volts();
static void adcCalibrateHVPS_Amps();

static volatile unsigned long int dwFilament__SetCurrent;
static volatile bool bFilament__EnableCurrent;

/*
    ADC counts to current or voltage:

        HCP 14-6500:        max. 6.5 kV, 2 mA <-> 0...10V

        0...5V <--> 3.25 kV, 1 mA
        5V <-> 1024 ADC counts
        1 ADC count <-> 0.0048828125V
            0.0048828125 <-> 0.003173828125 kV = 3.1738 V
                         <-> 0.0009765625 mA = 0.9765625 uA
*/
/*@
    requires (adcCounts >= 0) && (adcCounts < 1024);
*/
static inline uint16_t serialADC2VoltsHCP(
    uint16_t adcCounts,
    uint8_t channel
) {
    return (uint16_t)(((double)(adcCounts)) * cfgOptions.psuADCCalibration.channel[(channel-1)*2].k + cfgOptions.psuADCCalibration.channel[(channel-1)*2].d);
}
/*@
    requires (adcCounts >= 0) && (adcCounts < 1024);
    assigns \nothing;
*/
static inline uint16_t serialADC2TenthMicroampsHCP(
    uint16_t adcCounts,
    uint8_t channel
) {
    return (uint16_t)(((double)(adcCounts)) * cfgOptions.psuADCCalibration.channel[(channel-1)*2 + 1].k + cfgOptions.psuADCCalibration.channel[(channel-1)*2 + 1].d);
    /* return (uint16_t)((double)(adcCounts) * 9.765625); */
}
static inline uint16_t serialADC2MilliampsFILA(
    uint16_t adcCounts
) {
    uint16_t deviation;
    if(adcCounts < 512) {
        deviation = 512 - adcCounts;
    } else {
        deviation = adcCounts - 512;
    }
    return (uint16_t)(((double)deviation) * 4.8828125);
}

/*
    Ringbuffer utilis
*/
/*@
    predicate acsl_serialbuffer_valid(struct ringBuffer* lpBuf) =
        \valid(lpBuf)
        && \valid(&(lpBuf->dwHead))
        && \valid(&(lpBuf->dwTail))
        && (lpBuf->dwHead >= 0) && (lpBuf->dwHead < SERIAL_RINGBUFFER_SIZE)
        && (lpBuf->dwTail >= 0) && (lpBuf->dwTail < SERIAL_RINGBUFFER_SIZE);
*/
/*@
    requires lpBuf != NULL;
    requires \valid(lpBuf);
    requires \valid(&(lpBuf->dwHead));
    requires \valid(&(lpBuf->dwTail));

    assigns lpBuf->dwHead;
    assigns lpBuf->dwTail;

    ensures lpBuf->dwHead == 0;
    ensures lpBuf->dwTail == 0;
    ensures acsl_serialbuffer_valid(lpBuf);
*/
static inline void ringBuffer_Init(volatile struct ringBuffer* lpBuf) {
    #ifndef FRAMAC_SKIP
        uint8_t oldSREG = SREG;
            cli();
    #endif
    lpBuf->dwHead = 0;
    lpBuf->dwTail = 0;
    #ifndef FRAMAC_SKIP
        SREG = oldSREG;
    #endif
}
/*@
    requires lpBuf != NULL;
    requires acsl_serialbuffer_valid(lpBuf);

    assigns \nothing;

    ensures (\result == true) && (\result == false);
    ensures acsl_serialbuffer_valid(lpBuf);

    behavior isDataAvailable:
        assumes lpBuf->dwHead != lpBuf->dwTail;
        ensures \result == true;
    behavior noDataAvailable:
        assumes lpBuf->dwHead == lpBuf->dwTail;
        ensures \result == false;

    disjoint behaviors isDataAvailable, noDataAvailable;
    complete behaviors isDataAvailable, noDataAvailable;
*/
static inline bool ringBuffer_Available(volatile struct ringBuffer* lpBuf) {
    bool res;
    #ifndef FRAMAC_SKIP
        uint8_t oldSREG = SREG;
        cli();
    #endif
    res = (lpBuf->dwHead != lpBuf->dwTail) ? true : false;
    #ifndef FRAMAC_SKIP
        SREG = oldSREG;
    #endif
    return res;
}
/*@
    requires lpBuf != NULL;
    requires acsl_serialbuffer_valid(lpBuf);

    assigns \nothing;

    ensures (\result == true) || (\result == false);
    ensures acsl_serialbuffer_valid(lpBuf);

    behavior noSpaceAvailable:
        assumes ((lpBuf->dwHead + 1) % SERIAL_RINGBUFFER_SIZE) == lpBuf->dwTail;
        ensures \result == false;
    behavior spaceAvailable:
        assumes ((lpBuf->dwHead + 1) % SERIAL_RINGBUFFER_SIZE) != lpBuf->dwTail;
        ensures \result == true;

    disjoint behaviors noSpaceAvailable, spaceAvailable;
    complete behaviors noSpaceAvailable, spaceAvailable;
*/
static inline bool ringBuffer_Writable(volatile struct ringBuffer* lpBuf) {
    bool res;
    #ifndef FRAMAC_SKIP
        uint8_t oldSREG = SREG;
        cli();
    #endif
    res = (((lpBuf->dwHead + 1) % SERIAL_RINGBUFFER_SIZE) != lpBuf->dwTail) ? true : false;
    #ifndef FRAMAC_SKIP
        SREG = oldSREG;
    #endif
    return res;
}
/*@
    requires lpBuf != NULL;
    requires acsl_serialbuffer_valid(lpBuf);

    assigns \nothing;

    ensures \result >= 0;
    ensures \result < SERIAL_RINGBUFFER_SIZE;
    ensures acsl_serialbuffer_valid(lpBuf);

    behavior noWrapping:
        assumes lpBuf->dwHead >= lpBuf->dwTail;
        ensures \result == (lpBuf->dwTail - lpBuf->dwHead);
    behavior wrapping:
        assumes lpBuf->dwHead < lpBuf->dwTail;
        ensures \result == (SERIAL_RINGBUFFER_SIZE - lpBuf->dwTail) + lpBuf->dwHead;

    disjoint behaviors noWrapping, wrapping;
    complete behaviors noWrapping, wrapping;
*/
static inline unsigned long int ringBuffer_AvailableN(volatile struct ringBuffer* lpBuf) {
    unsigned long int res;
    #ifndef FRAMAC_SKIP
        uint8_t oldSREG = SREG;
        cli();
    #endif

    if(lpBuf->dwHead >= lpBuf->dwTail) {
        res = lpBuf->dwHead - lpBuf->dwTail;
    } else {
        res = (SERIAL_RINGBUFFER_SIZE - lpBuf->dwTail) + lpBuf->dwHead;
    }

    #ifndef FRAMAC_SKIP
        SREG = oldSREG;
    #endif
    return res;
}
/*@
    requires lpBuf != NULL;
    requires acsl_serialbuffer_valid(lpBuf);

    assigns \nothing;

    ensures \result >= 0;
    ensures \result < SERIAL_RINGBUFFER_SIZE;
    ensures acsl_serialbuffer_valid(lpBuf);

    behavior noWrapping:
        assumes lpBuf->dwHead >= lpBuf->dwTail;
        ensures \result == SERIAL_RINGBUFFER_SIZE - (lpBuf->dwTail - lpBuf->dwHead) - 1;
    behavior wrapping:
        assumes lpBuf->dwHead < lpBuf->dwTail;
        ensures \result == SERIAL_RINGBUFFER_SIZE - ((SERIAL_RINGBUFFER_SIZE - lpBuf->dwTail) + lpBuf->dwHead) - 1;

    disjoint behaviors noWrapping, wrapping;
    complete behaviors noWrapping, wrapping;
*/
static inline unsigned long int ringBuffer_WriteableN(volatile struct ringBuffer* lpBuf) {
    return SERIAL_RINGBUFFER_SIZE - ringBuffer_AvailableN(lpBuf);
}
/*@
    requires lpBuf != NULL;
    requires acsl_serialbuffer_valid(lpBuf);

    ensures (\result >= 0) && (\result <= 0xFF);
    ensures acsl_serialbuffer_valid(lpBuf);

    behavior emptyBuffer:
        assumes lpBuf->dwHead == lpBuf->dwTail;

        assigns \nothing;

        ensures \result == 0x00;
        ensures lpBuf->dwTail == \old(lpBuf->dwTail);
    behavior availableData:
        assumes lpBuf->dwHead != lpBuf->dwTail;

        assigns lpBuf->dwTail;

        ensures \result == lpBuf->buffer[\old(lpBuf->dwTail)];
        ensures lpBuf->dwTail == ((\old(lpBuf->dwTail)+1) % SERIAL_RINGBUFFER_SIZE);

    disjoint behaviors emptyBuffer, availableData;
    complete behaviors emptyBuffer, availableData;
*/
static unsigned char ringBuffer_ReadChar(volatile struct ringBuffer* lpBuf) {
    char t;

    #ifndef FRAMAC_SKIP
        uint8_t oldSREG = SREG;
        cli();
    #endif

    if(lpBuf->dwHead == lpBuf->dwTail) {
        return 0x00;
    }

    t = lpBuf->buffer[lpBuf->dwTail];
    lpBuf->dwTail = (lpBuf->dwTail + 1) % SERIAL_RINGBUFFER_SIZE;

    #ifndef FRAMAC_SKIP
        SREG = oldSREG;
    #endif

    return t;
}
/*@
    requires lpBuf != NULL;
    requires acsl_serialbuffer_valid(lpBuf);

    assigns \nothing;

    ensures (\result >= 0) && (\result <= 0xFF);
    ensures acsl_serialbuffer_valid(lpBuf);
    ensures lpBuf->dwTail == \old(lpBuf->dwTail);

    behavior emptyBuffer:
        assumes lpBuf->dwHead == lpBuf->dwTail;
        assigns \nothing;
        ensures \result == 0x00;
    behavior availableData:
        assumes lpBuf->dwHead != lpBuf->dwTail;
        assigns \nothing;
        ensures \result == lpBuf->buffer[\old(lpBuf->dwTail)];

    disjoint behaviors emptyBuffer, availableData;
    complete behaviors emptyBuffer, availableData;
*/
static unsigned char ringBuffer_PeekChar(volatile struct ringBuffer* lpBuf) {
    unsigned char res = 0x00;

    #ifndef FRAMAC_SKIP
        uint8_t oldSREG = SREG;
        cli();
    #endif

    if(lpBuf->dwHead != lpBuf->dwTail) {
        res = lpBuf->buffer[lpBuf->dwTail];
    }

    #ifndef FRAMAC_SKIP
        SREG = oldSREG;
    #endif
    return res;
}

/*@
    requires lpBuf != NULL;
    requires acsl_serialbuffer_valid(lpBuf);
    requires (dwDistance < SERIAL_RINGBUFFER_SIZE);

    assigns \nothing;

    ensures (\result >= 0) && (\result <= 0xFF);
    ensures acsl_serialbuffer_valid(lpBuf);
    ensures lpBuf->dwTail == \old(lpBuf->dwTail);

    behavior emptyBuffer:
        assumes lpBuf->dwHead == lpBuf->dwTail;
        assigns \nothing;
        ensures \result == 0x00;
    behavior distanceInRange:
        assumes ((lpBuf->dwHead > lpBuf->dwTail) && (dwDistance < (lpBuf->dwTail - lpBuf->dwHead))) || ((lpBuf->dwHead < lpBuf->dwTail) && (dwDistance < (SERIAL_RINGBUFFER_SIZE - lpBuf->dwTail) + lpBuf->dwHead));
        assigns \nothing;
        ensures \result == lpBuf->buffer[(\old(lpBuf->dwTail) + dwDistance) % SERIAL_RINGBUFFER_SIZE];
    behavior availableData:
        assumes ((lpBuf->dwHead > lpBuf->dwTail) && (dwDistance >= (lpBuf->dwTail - lpBuf->dwHead))) || ((lpBuf->dwHead < lpBuf->dwTail) && (dwDistance >= (SERIAL_RINGBUFFER_SIZE - lpBuf->dwTail) + lpBuf->dwHead));
        assigns \nothing;
        ensures \result == 0x00;

    disjoint behaviors emptyBuffer, availableData;
    complete behaviors emptyBuffer, availableData;
*/
static unsigned char ringBuffer_PeekCharN(
    volatile struct ringBuffer* lpBuf,
    unsigned long int dwDistance
) {
    unsigned char res = 0x00;

    #ifndef FRAMAC_SKIP
        uint8_t oldSREG = SREG;
        cli();
    #endif

    if(lpBuf->dwHead != lpBuf->dwTail) {
        if(ringBuffer_AvailableN(lpBuf) > dwDistance) {
            res = lpBuf->buffer[(lpBuf->dwTail + dwDistance) % SERIAL_RINGBUFFER_SIZE];
        }
    }

    #ifndef FRAMAC_SKIP
        SREG = oldSREG;
    #endif

    return res; 
}
/*@
    requires lpBuf != NULL;
    requires acsl_serialbuffer_valid(lpBuf);
    requires ((lpBuf->dwHead > lpBuf->dwTail) && (dwCount <= (lpBuf->dwTail - lpBuf->dwHead))) || ((lpBuf->dwHead < lpBuf->dwTail) && (dwCount <= (SERIAL_RINGBUFFER_SIZE - lpBuf->dwTail) + lpBuf->dwHead));
    requires (dwCount >= 0);

    assigns lpBuf->dwTail;

    ensures lpBuf->dwTail == ((\old(lpBuf->dwTail) + dwCount) % SERIAL_RINGBUFFER_SIZE);
    ensures acsl_serialbuffer_valid(lpBuf);
*/
static inline void ringBuffer_discardN(
    volatile struct ringBuffer* lpBuf,
    unsigned long int dwCount
) {
    #ifndef FRAMAC_SKIP
        uint8_t oldSREG = SREG;
        cli();
    #endif
    lpBuf->dwTail = (lpBuf->dwTail + dwCount) % SERIAL_RINGBUFFER_SIZE;
    #ifndef FRAMAC_SKIP
        SREG = oldSREG;
    #endif
    return;
}
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

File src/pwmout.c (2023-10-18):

#include <avr/io.h>
#include <avr/interrupt.h>
#include <stdint.h>

#define PWM_VPERDIVK (3.24781922941*0.899405351856)
#define PWM_VPERDIVW (3.49231230262*0.899009900992)
#define PWM_VPERDIVFOC 3.137850885
#define PWM_VPERDIV4 3.1914893617
#define PWM_VPERUA 0.979959039479
#define PWM_FILA_VPERDIV 0.224609375

// V / PWM_VPERDIVK
/*
 #define PWM_MAX_DIFFERENCE_W_K_POS 32 
 #define PWM_MAX_DIFFERENCE_W_K_NEG 15 
*/
#define PWM_MAX_DIFFERENCE_W_K_PV 100
#define PWM_MAX_DIFFERENCE_W_K_NV 15

#define VMAXSLOPE_V_PER_S 12

#include "./sysclock.h"
#include "./pwmout.h"
#include "./psu.h"
#include "./serial.h"

#ifdef __cplusplus
    extern "C" {
#endif

/*
    Clock source will be timer2

    Running with one of the following settings:
            Prescaler               Frequency               OCR1A           Prescaler val
            /1                      8 MHz                   -               0x01
            /8                      1 MHz                   -               0x02
            /32                     500 kHz                 1               0x03
            /64                     250 kHz                 16              0x04
            /128                    125 kHz                 1               0x05
            /256                    62.5 kHz                1               0x06
            /1024                   15.625 kHz              1               0x07

    Values that seem to work +- relieable:
        Prescaler 0x04 (/64 -> 250 KHz), Overflow counter 0x10 (16) -> PWM coutner freq. 15.625 kHz)
*/
#define PWM_TIMERTICK_PRESCALER             0x06
#define PWM_TIMERTICK_OVERFLOWVAL           0x02

static uint16_t pwmoutOnCyclesReal[8];
uint16_t pwmoutOnCycles[8];
static uint16_t pwmoutCurrentCycles[8];
static bool bFilamentOn;

static uint16_t slopeUpdateInterval = 0;

ISR(TIMER2_COMPA_vect) {
    uint8_t i;

    /*
        Implement a slope limit (limiting maximum dV/dt) on voltage
    */
    if(slopeUpdateInterval == 2048) {
        for(i = 0; i < sizeof(pwmoutCurrentCycles)/sizeof(uint16_t)-1; i=i+1) {
            if((i & 0x01) == 0) {
                if(pwmoutOnCyclesReal[i] > pwmoutOnCycles[i]) {
                    pwmoutOnCyclesReal[i] =  ((pwmoutOnCyclesReal[i] - pwmoutOnCycles[i]) > VMAXSLOPE_V_PER_S) ? (pwmoutOnCyclesReal[i] - VMAXSLOPE_V_PER_S) : pwmoutOnCycles[i];
                } else if(pwmoutOnCyclesReal[i] < pwmoutOnCycles[i]) {
                    pwmoutOnCyclesReal[i] =  ((pwmoutOnCycles[i] - pwmoutOnCyclesReal[i]) > VMAXSLOPE_V_PER_S) ? (pwmoutOnCyclesReal[i] + VMAXSLOPE_V_PER_S) : pwmoutOnCycles[i];
                }

                /* Set enable and disable for output according to set output voltage */
                if(pwmoutOnCyclesReal[i >> 1] != 0) {
                    psuStates[i >> 1].bOutputEnable = true;
                } else {
                    psuStates[i >> 1].bOutputEnable = false;
                }
            } else {
                pwmoutOnCyclesReal[i] = pwmoutOnCycles[i];
            }
        }
	    /* Verify that W and K are not spaced too far ...  if they are clamp */
#if 0
	    {
	        unsigned long int diff;
	        if(pwmoutOnCyclesReal[0] > pwmoutOnCyclesReal[2]) {
	            diff = pwmoutOnCyclesReal[0] - pwmoutOnCyclesReal[2];
	            if(diff > PWM_MAX_DIFFERENCE_W_K_NEG) {
	                pwmoutOnCyclesReal[2] = pwmoutOnCyclesReal[0] - PWM_MAX_DIFFERENCE_W_K_NEG;
	            }
	        } else {
	            diff = pwmoutOnCyclesReal[2] - pwmoutOnCyclesReal[0];
	            if(diff > PWM_MAX_DIFFERENCE_W_K_POS) {
	                pwmoutOnCyclesReal[2] = pwmoutOnCyclesReal[0] + PWM_MAX_DIFFERENCE_W_K_POS;
	            }
	        }
	    }
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

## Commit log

2021-07-07 Implemented simple ID command, simply dumping serial response currently
2021-07-07 Added pin assignment and ID command
2021-07-07 Added mapping to pin/port pairs
2021-07-08 Removed NULL byte transmitted after current messages
2021-07-09 Added external declaration for current ADC values
2021-07-09 Added support for current and voltage measurement (raw ADC counts)
2021-07-09 HCP: Implemented query functions for current and voltage
2021-07-09 Updated voltage measurement calibration ...
2021-07-13 Added PWM routines to set voltage and current and provided coarse calibration
2021-07-13 Implemented set voltage and set current
2021-07-13 Adding current version
2021-08-16 New assignment for A8 for current measurement
2021-08-16 Add support to read filament current in host CLI tool
2021-08-16 Added support for filament current sensor
2021-08-17 Added host library support to send filament on/off and set filament current commands
2021-08-17 Off now also disabled filament current
2021-08-17 Implemented setting filament current (duty cycle, not mA currently)
2021-08-17 Implemented mode detection (off / voltage controlled / current limited) in serial handler
2021-08-18 Beam on now honors filament current setting, better reporting, ramp works, off disables PSUs
2021-08-19 Moved current ramp in front of HV ramp to prevent cathode stripping
2021-08-20 Added current measurement output to message
2021-08-20 Pushing current firmware revision
2022-05-02 Added atexit routine to release serial port and shutdown thread
2022-05-04 Overcurrent detection only triggers if set voltage is not zero
2022-05-04 Off also sets voltages to 0
2022-05-04 Speed up filament heating by 1/3
2022-07-20 Added quakEstimateBeamCurrent project specific beam current estimation
2022-07-20 Raising exception in beam current estimation method when not connected
2022-07-26 MQTT client side topic filter (sometimes used)
2022-09-20 Now Whenelt and Focus work again as expected as current sinks in the QUAK/ESR experiment
2022-09-20 Disable currently unused logging port
2022-10-10 Added current setting method for power supplies
2022-10-21 Update to use secondary current controller board instead of PWM via SSR
2022-10-21 Firmware now counts filament current in 0.1 mA
2022-10-21 Always reporting SET current even if disabled
2022-10-21 Python library now allows setting filament current in 100 uA steps
2022-10-24 Placeholder for current controller extension responses
2022-11-04 Began schematic for DAC & ADC based interface and controller board
    [interfaceboard.kicad_pcb, interfaceboard.kicad_sch]
2022-11-04 Finished schematic
    [interfaceboard.kicad_sch]
2022-11-07 FInished Schematic, assigned footprints, added 230V PSU
    [interfaceboard.kicad_sch]
2022-11-07 Began place and route
    [interfaceboard.kicad_pcb]
2022-11-08 Continue place and route, minor fixes
    [interfaceboard.kicad_pcb, interfaceboard.kicad_sch]
2022-11-11 Controller:
    * Implemented slope limit for high voltages
    * Removed redundant constants to reduce memory usage
    * Output enable / disable is now controlled by voltage on HV supplies (to guarantee ramping operation)
    * Removed code for controlling primary side SSR
    * Removed serial commands that allowed enabling / disabling PSUs (since this is now controlled by voltage setting)
    * Reduced sized of parsing buffers for complete messages
2022-11-11 Modified to match firmware, version 0.0.26
    * Removed setPSUEnable and setPSUDisable (not supported by controller any more)
    * Unit conversion of current is handled in firmware for setting filament current
    * Filament current report is now correctly parsed also for seta: responses
2022-11-22 Bugfixes and new features for 0.0.36
    * Ringbuffer always keeps a single byte empty to prevent overrun
    * Fixed bug in isAvailable that inverted correct result
    * Allows to disable shutdown at interpreter exit (shutdown_on_terminate(False))
    * Beamon timeout increased to 1200 seconds
    * Synchronous waiting for filseta on filon, filoff and setting filament current
    * Scaling of filament current
    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
2022-11-25 Added support to set filament current in beamOn command
2022-12-02 Invalid correction factor for currents in __str__
2022-12-06 Allow calibration of ADC readings from HVPS
2022-12-06 Methods for calibration of HVPS readings
2022-12-06 Waiting for stable voltages on HVPS (only works after calibration)
2023-10-18 Getting target voltages fixed
2023-10-18 Fixed current setting, bump version
2023-10-18 Removing querying of target voltage and current limit for beam mode on serial0 to save progmem
2023-10-18 New calibrations
